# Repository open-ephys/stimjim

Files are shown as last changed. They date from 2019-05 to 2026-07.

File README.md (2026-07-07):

Stimjim - a flexible, precise, and inexpensive open-source stimulator
-------------------------------
Stimjim is a current and voltage stimulator for stimulating neural tissue (as with stimulating electrodes). 

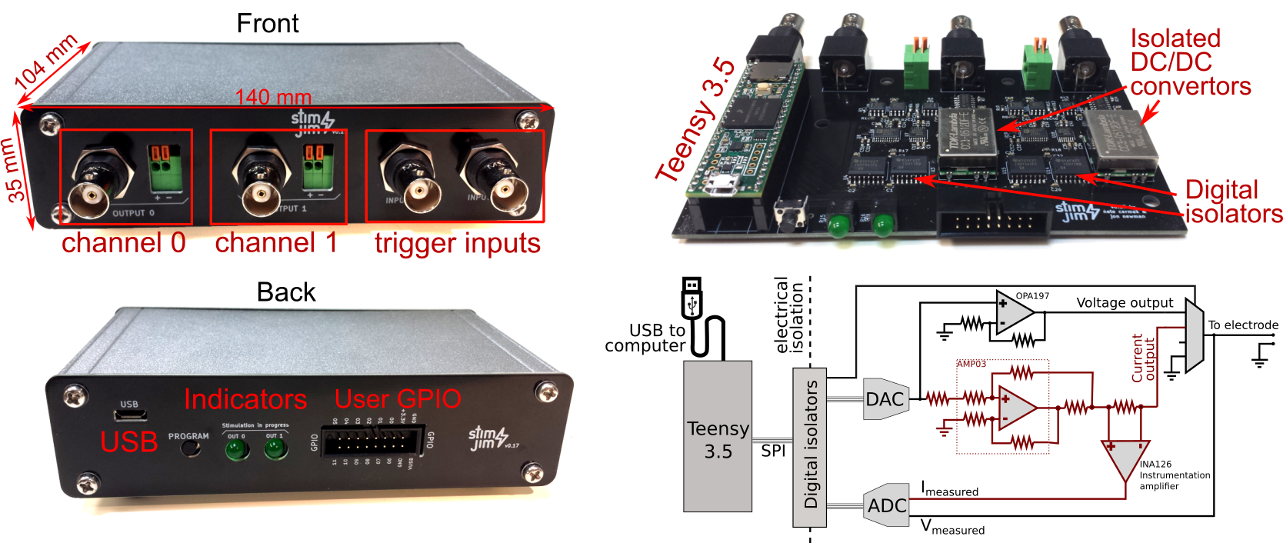
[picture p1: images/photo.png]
Stimjim picture


# Specifications:

 - Two independently-controllable output channels, each with both current and voltage output modes
 - Output range in current mode: -3.33mA to +3.33mA. 
 - Output range in voltage mode: -15V to 15V.
 - Pulse width down to 0.02 ms (as configured with default firmware)
 - Compliance voltage is +-13.7V in current mode (+/-3.33uA output possible for resistances up to 4k, +-137uA possible for resistances up to 100k)
 - Powered by USB
 - Channels are isolated from power supply and from each other.
 - Onboard ADC measurement of actual output current or voltage
 
# Building your own Stimjim:

Here are the steps to build your very own Stimjim box. 

### Option 1: Assemble (solder components onto) the board yourself.

1. Order printed circuit boards (PCBs) for the [main board](./PCB/stimjimFabricationFiles_v0.181.zip) (4-layer, 129x79.5 mm, otherwise standard order parameters) and the [enclosure front and back panels](./PCB/stimjimPanelFabricationFiles_v0.18.zip) (1-layer, 2 designs, total size 140x71 mm) from [JLCPCB](https://jlcpcb.com/), [Seeedstudio](https://www.seeedstudio.com/fusion_pcb.html) or any other PCB manufacturer. Note that for the panels, the PCB manufacturer may alert you to the fact that there is no exposed copper. This is correct, there should be a copper layer entirely covered by soldermask.
2. Order [components](./stimjim_BOM.xlsx) (entirely from [Digikey](https://www.digikey.com/)).
3. Solder components onto the PCB, using the [schematic](./schematic.pdf) and [layout](./pcb.pdf) files for reference. This may take a few hours, depending on your soldering experience and capability. I typically use a pair of good tweezers, leaded solder paste, and a soldering iron, although a reflow oven also will work as well and may be easier.

### Option 2: Use [SeeedStudio's assembly service](https://www.seeedstudio.com/fusion_pcb.html). 
Recent estimate is about $800 for two assembled boards, plus another roughly $100 for the enclosure and panels. Thanks to Vincent Prevosto for trying this out and submitting these instructions!

1.  The main board PCB and components can be ordered and assembled together on SeeedStudio.
    To order assembled boards, go to [https://www.seeedstudio.com/fusion_pcb.html](https://www.seeedstudio.com/fusion_pcb.html).
   
    *   Click on **Add Gerber Files** and upload [the main board Gerber files](./PCB/stimjimFabricationFiles_v0.181.zip). 
        Make sure to select 4 layers and enter correct dimensions (129x79.5 mm). 
        Select PCB quantity (minimum 5).
    *   Move now to the **PCB Assembly** section.
    *   Click on **Add Assembly Drawing & Pick and Place File** and upload the [zip file containing pdf assembly files and position files](./PCB/stimjim_SeeedStudioAssembly_PickAndPlace.zip).
    *   Select the requested PCB assembly quantity (tested with 2 for $780 USD in late 2019).
    *   Click on **Add BOM File** and upload the [Seeedstudio-formatted Bill of Materials](./PCB/stimjim_SeeedStudioAssembly_BOM.xlsx). The service will check parts availability. Seeedstudio may not be able to provide an instant quote, but they should send you one within a day.
    *   Seeedstudio-assembled Stimjims have been successfully tested by one user, but you have the option to have SeeedStudio test the assembly as well.
   
2. Order the [front and back panels for the enclosure](./PCB/stimjimPanelFabricationFiles_v0.18.zip) (1-layer, 2 designs, total size 140x71 mm) from [Seeedstudio](https://www.seeedstudio.com/fusion_pcb.html), [JLCPCB](https://jlcpcb.com/) or any other PCB company you like.
3. Order the enclosure itself (see the line "enclosure" in the [Bill of materials](./stimjim_BOM.xlsx)) from [Digikey](https://www.digikey.com/).

### Continuing from either option 1 or 2:

4.  Put the main board inside the enclosure (bottom slot), and screw the panels onto the front and back of the enclosure. 
5.  Connect the Stimjim to the computer via USB. Compile and download the [firmware](./stimjimPulser/) onto the Teensy, using the [Arduino IDE](https://www.arduino.cc/en/main/software) with [Teensyduino](https://www.pjrc.com/teensy/td_download.html) installed (or write your own!). Before compiling stimjimPulser.ino, You will need to install the Stimjim library by copying the [stimjim library folder](./lib/) to the appropriate arduino "libraries" folder on your computer. On Windows, this is typically My Documents/Arduino/libraries and on linux it is typically ~/Arduino/libraries. 
6.  Upon bootup, Stimjim should self-report (via the serial connection, visible using the "Serial Monitor" tool in the Arduino IDE) on a handful of calibration routines it runs. Example output looks as follows:

	    Booting StimJim on Teensy 3.5!
	    Initializing inputs...
	    ADC offsets (+-2.5V): -11.030000, -11.150000
	    ADC offsets (+-10V): -10.220000, -10.340000
	    current offsets: 11, 8
	    voltage offsets: 0, 0
	    Ready to go!
	   
	The ADC offsets indicate the ADC reading (in ADC units, 2.4mV per ADC unit) from the output when the output is grounded, for channels 0 and 1, respectively. The ADC typically has a small but nonzero "Zero offset error" which is the reading when it should be reading exactly 0V. Stimjim measures this error (with two different range settings) and corrects all subsequent readings. We typically see values less than 20 - a value of +-4096 indicates some sort of problem with the board.
	
	Current offsets are the raw value of the DAC output (-32768 to 32767) that yields the current reading closest to 0uA. This offset is also used in subsequent stimulation to avoid any small but consistent DC current during pulses.

# Getting started using Stimjim:

To generate a pulse train, you first need to send a serial command, terminated by a newline (\n) in order to define a PulseTrain. An example command would be:

    S0,0,1,2000,1000000; 100,0,150; -100,-100,200
   
The "S" is to *s*pecify the parameters of a pulse train, and the zero immediately following the S implies that we are going to set parameters for PulseTrain 0. The code provided here allows Stimjim to store 100 different PulseTrain parameter sets. If any comma- and semicolon-separated numbers appear following the S, they are the pulse train parameters. A command that simply consists of "S0" will result in simply printing out the current parameters of PulseTrain 0. 

Once a PulseTrain is defined, to run it you would send a command of the form:

    T0

This tells Stimjim to start running PulseTrain 0. If we had parameterized PulseTrain #3, we could just as easily run PulseTrain #3 with the command "T3".

##  Parameterization 



The numbers that come after an "S" indicate parameters as denoted below:

1. [PulseTrain number], 
2. [output 0 mode],
3. [output 1 mode],
4. [period],
5. [duration];
6. [mV or uA for stage 0 output 0],
7. [mV or uA for stage 0 output 1],
8. [stage 0 duration (us)]; 
9. [mV or uA for stage 1 output 0],
10. [mV or uA for stage 1 output 1],
11. [stage 1 duration (us)];
12. (etc for additional stages, up to 10 total stages).

After the "S", the first parameter is the number of the PulseTrain that we are defining. The next two parameters are the modes of each output channels. Modes are as follows:

 - 0 = Voltage output
 - 1 = Current output
 - 2 = Output is disconnected
 - 3 = Output is grounded

Our example command above was: 
   
    S0,0,1,2000,1000000; 100,0,150; -100,-100,200
   
In this example, output 0 is generating a voltage output (mode 0), and output 1 is generating a current output (mode 1). To specify that a channel should not output anything during a pulse train, set the mode to 3 (ground).  

The fourth parameter is the _period_ of the pulse train. In this example, pulses are delivered every 2000 us (2 ms).

The fifth parameter is the _duration_ of the pulse train, in microseconds. In the example, the pulse train lasts for one second (1000000 microseconds).

Parameters after the 5th come in sets of 3, and describe a "stage" of a pulse in the train.  The first two parameters are the amplitude (in mV or uA, depending on whether the output is voltage or current) of each channel during that stage, and the third is the duration (in microseconds) of that stage. Note that a semi-colon is before the beginning of each set of 3, and the three parameters themselves are separated from each other by commas.

In the example given above, there are two stages to each pulse. In the first, channel 0 outputs 100mV, channel 1 outputs nothing, and that lasts for 150 usec. Then channel 0 switches to outputting -100mV, and channel 2 outputs -100uA for 200 usec. 

## Triggering
Stimjim can utilize trigger signals from its BNC inputs. To make a rising edge on input 0 trigger PulseTrain 1, send the command

	R0,1

To make a rising edge on input 1 trigger PulseTrain 2

	R1,2
	
And finally, to make a falling edge on input 1 trigger PulseTrain 2:

	R1,2,1

The final argument for the R command is optional, and defaults to 0 (rising edge).

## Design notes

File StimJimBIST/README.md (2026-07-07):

# StimJimBIST
A simple console application that performs built in evaluation of the funcationility
of both stimulation channels.

Limitations:
- Assumes that StimJimPulser is loaded onto the Teensy
- Does not test physical connectivity (solder joints) of BNCS, screw-terminals
- Does not test trigger or GPIO capabilities
- Assumes there is nothing connected to the output channels of the device

### Usage
Usage:
```
StimJimBIST COM3
```

Example result:
```
Running StimJim BIST.
Testing voltage mode.

Channel 0:
| Test V. | Meas V. | Err. mV. | Pass / Fail | Test uA. | Meas uA. | Err. uA | Pass / Fail |
|---------|---------|----------|-------------|----------|----------|---------|-------------|
| -9.00   | -8.99   | 7        | PASS        | -1993.36 | -1987.00 | 6.36    | PASS        |
| 0.00    | 0.01    | 7        | PASS        | 0.00     | 0.00     | 0.00    | PASS        |
| 9.00    | 9.01    | 5        | PASS        | 1993.36  | 1982.00  | -11.36  | PASS        |

Channel 1:
| Test V. | Meas V. | Err. mV. | Pass / Fail | Test uA. | Meas uA. | Err. uA | Pass / Fail |
|---------|---------|----------|-------------|----------|----------|---------|-------------|
| -9.00   | -9.00   | 3        | PASS        | -1993.36 | -1985.00 | 8.36    | PASS        |
| 0.00    | 0.01    | 5        | PASS        | 0.00     | 0.00     | 0.00    | PASS        |
| 9.00    | 9.02    | 19       | PASS        | 1993.36  | 1984.00  | -9.36   | PASS        |

Testing current mode.

Channel 0:
| Pol. | Meas V. | Err. mV. | Pass / Fail | Meas uA. | Err. uA | Pass / Fail |
|------|---------|----------|-------------|----------|---------|-------------|
| -    | -9.98   | 21       | PASS        | -4.00    | -4.00   | PASS        |
| +    | 10.01   | 6        | PASS        | 0.00     | 0.00    | PASS        |

Channel 1:
| Pol. | Meas V. | Err. mV. | Pass / Fail | Meas uA. | Err. uA | Pass / Fail |
|------|---------|----------|-------------|----------|---------|-------------|
| -    | -9.97   | 27       | PASS        | -4.00    | -4.00   | PASS        |
| +    | 10.01   | 12       | PASS        | 0.00     | 0.00    | PASS        |

GLOBAL RESULT: PASS
```

### Explanation

#### Voltage Mode test
This test examines the functionality of the DAC, ADC, output mux, current source, and current sense circuit simultaneously.

- Put both channels in voltage mode ()
	- This this ties V_OUT to CHANNEL_OUT, which is open
	- This ties I_OUT to ground through a 1k resistor
	- I_OUT = V_OUT / 3kOhm
	
- For each channel, apply -9V, 0V, and 9V to V_OUT
	- This sets V_DAC = V_OUT / 1.5
	- V_DAC is still applied to Howland and current measurement circuit with transimpedance gain of 0.33 mA per volt
	- Read the voltage at CHANNEL_OUT to see if the voltage iset to the test voltage
	- Read I_SENSE to see that its equal to V_DAC / 1.5 * 0.33 mA/V

#### Current Mode test
This test examines the functionality of the DAC, ADC, and output mux, and current sense circuit simultaneously.
It is largely redundant with the first test but does ensure that the output mux can switch to a non default state.

- Put both channels in current mode
	- This ties V_OUT to floating
    - This ties I_OUT to CHANNEL_OUT, which is open

- For each channel, attempt to apply  -1V, 1V to V_OUT
	- This sets V_DAC = V_OUT / 1.5
	- This attempts to deliver V_DAC * 0.33 mA/V to CHANNEL_OUT
	- Read the voltage at CHANNEL_OUT (should saturate at +/-10V)
	- Read current through CHANNEL_OUT (should be 0 since its open)

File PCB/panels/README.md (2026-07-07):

EXN-23359.DXF is the original outline of the extruded aluminum enclosure. It was
edited in panel-outline.SLDPRT to remove some of the finer features of the
aluminum enclosure that might not be good PCB DFM. I extruded the sketch in
panel-outline.SLDPRT because exporting the sketch by itself was presenting buggy
behavior wherein not all lines of the sketch were actually exported into the
resulting DXF. Instead, I export the outline of the extruded part which doesn't
present this buggy behavior. panel-outline.SLDPRT is exported to
panel-outline.DXF which is subsequently imported into the KiCAD PCB panel files
as a graphic.

The channel-design.SLDPRT is used to create the silkscreen design for each channel.

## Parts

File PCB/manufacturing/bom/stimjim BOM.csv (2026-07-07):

# | Qty | Reference | Value | Tolerance | Footprint | TempCo | Voltage | DNP | OEPSPN | MPN | Description
1 | 40 | C1,C2,C6,C7,C9,C11,C13,C14,C16,C17,C18,C20,C22,C23,C24,C25,C26,C27,C31,C32,C34,C35,C38,C39,C41,C42,C43,C44,C47,C48,C49,C50,C63,C65,C66,C67,C80,C82,C89,C90 | 0.1uF |  | Capacitor_SMD:C_0603_1608Metric |  |  |  | OEPS010009 | GRM188R72A104KA35D | CAPACITOR: SMD CER 0603 100nF 100V ±10% X7R [GRM188R72A104KA35D] [SMD]
2 | 6 | C3,C4,C5,C28,C29,C30 | 10uF |  | Capacitor_SMD:C_1206_3216Metric_Pad1.33x1.80mm_HandSolder |  | 25V |  | OEPS010094 | GRT319R6YA106KE01D | CAPACITOR: SMD CER 1206 10uF 35V ±10% X5R [GRT319R6YA106KE01D] [SMD]
3 | 12 | C8,C10,C12,C15,C33,C36,C37,C40,C51,C52,C295,C297 | 1uF |  | Capacitor_SMD:C_0603_1608Metric | X5R | 25V |  | OEPS010022 | CL10A105KA8NNNC | CAPACITOR: SMD CER 0603 1uF 25V ±10% X5R [CL10A105KA8NNNC] [SMD]
4 | 4 | C19,C21,C45,C46 | 0.01uF |  | Capacitor_SMD:C_0603_1608Metric |  |  |  | OEPS010074 | C1608X7R1H103K080AA | CAPACITOR: SMD CER 0603 10nF 50V ±10% X7R [C1608X7R1H103K080AA] [SMD]
5 | 2 | C53,C54 | 2.2nF |  | Capacitor_SMD:C_1210_3225Metric_Pad1.33x2.70mm_HandSolder |  |  | DNP | OEPS000000 | DNP | DNP: Do Not Populate (DNI)
6 | 12 | C55,C56,C57,C58,C59,C60,C61,C62,C64,C81,C83,C84 | 0.1uF |  | Capacitor_SMD:C_0402_1005Metric | X7R |  |  | OEPS010050 | C1005X7R1E104K050BB | CAPACITOR: SMD CER 0402 100nF 25V ±10% X7R (OEPS H02 001) [C1005X7R1E104K050BB] [SMD]
7 | 8 | C68,C69,C72,C73,C74,C75,C76,C77 | 10uF |  | Capacitor_SMD:C_0603_1608Metric |  |  |  | OEPS010093 | GRM188R6YA106MA73J | CAPACITOR: SMD CER 0603 10uF 35V ±20% X5R [GRM188R6YA106MA73J] [SMD]
8 | 2 | C70,C71 | 22p |  | Capacitor_SMD:C_0402_1005Metric |  |  |  | OEPS010080 | CL05C220JB51PNC | CAPACITOR: SMD CER 0402 22pF 50V ±5% C0G/NP0 [CL05C220JB51PNC] [SMD]
9 | 2 | C78,C79 | 10p |  | Capacitor_SMD:C_0603_1608Metric |  |  |  | OEPS010096 | C0603C100J5GACTU | CAPACITOR: SMD CER 0603 10pF 50V ±5% C0G [C0603C100J5GACTU] [SMD]
10 | 4 | C85,C86,C87,C88 | 4.7u |  | Capacitor_SMD:C_0402_1005Metric | X5R | 16V |  | OEPS010097 | KGM05CR51C475MH | CAPACITOR: SMD CER 0402 4.7uF 16V ±20% X5R [KGM05CR51C475MH] [SMD]
11 | 4 | C91,C92,C93,C94 | 4.7u |  | Capacitor_SMD:C_0603_1608Metric |  |  |  | OEPS010047 | GRM188R61E475KE11D | CAPACITOR: SMD CER 0603 4.7uF 25V ±10% X5R (OEPS J05 009) [GRM188R61E475KE11D] [SMD]
12 | 10 | D1,D6,D8,D10,D11,D12,D13,D14,D15,D16 | BAT54SW |  | Package_TO_SOT_SMD:SOT-323_SC-70 |  |  |  | OEPS030056 | BAT54SW | DIODE: DIODE SCHOTTKY 30V 340mA ARRAY [BAT54SW] [TH]
13 | 3 | D3,D4,D5 | LED |  | open-ephys:LUMEX_SSF-LHXH100GD-01 |  |  |  | OEPS030055 | SSF-LXH100GD-01 | DIODE: LED TH Green 565nm 20mA R/A [SSF-LXH100GD-01] [TH]
14 | 1 | D9 | TPD4E05U06DQA |  | Package_SON:USON-10_2.5x1.0mm_P0.5mm |  |  |  | OEPS030037 | TPD4E05U06DQAR | DIODE: TVS DIODE 5.5VWM 14VC [TPD4E05U06DQAR] [10-UFDFN]
15 | 1 | J1 | 302-R161 |  | Connector_IDC:IDC-Header_2x08_P2.54mm_Horizontal |  |  |  | OEPS070152 | 302-R161 | CONNECTOR: HEADER 2.54MM R/A 2x8POS [302-R161] [TH]
16 | 4 | J2,J3,J7,J9 | 0731375003 |  | Connector_Coaxial:BNC_Amphenol_B6252HB-NPP3G-50_Horizontal |  |  |  | OEPS070151 | 0731375003 | CONNECTOR: BNC JACK 50ohm R/A [0731375003] [TH]
17 | 1 | J4 | 10129383-910002ALF |  | Connector_PinHeader_2.54mm:PinHeader_2x04_P2.54mm_Vertical_SMD |  |  | DNP | OEPS070120 | 10129383-910002ALF | CONNECTOR: HEADER VERT 2x5POS 2.54MM [10129383-910002ALF] [SMD]
18 | 1 | J10 | USB4105-GF-A |  | Connector_USB:USB_C_Receptacle_GCT_USB4105-xx-A_16P_TopMnt_Horizontal |  |  |  | OEPS070105 | USB4105-GF-A | CONNECTOR: USB2.0 TYPE C 24P SMD R/A [USB4105-GF-A] [SMD/TH]
19 | 1 | J11 | BM03B-SRSS-TB |  | Connector_JST:JST_SH_BM03B-SRSS-TB_1x03-1MP_P1.00mm_Vertical |  |  | DNP | OEPS070121 | BM03B-SRSS-TB | CONNECTOR: HEADER VERT 3POS 1MM [BM03B-SRSS-TB] [SMD]
20 | 1 | L1 | AOTA-B201610S3R3-101-T |  | open-ephys:L_Abracon_2x1.6x1.0mm |  |  |  | OEPS040036 | AOTA-B201610S3R3-101-T | INDUCTOR: FIXED INDUCTOR SMD 3.3uH 2.1A 140mΩ [AOTA-B201610S3R3-101-T] [0806]
21 | 1 | N1 | SMTRAM3-7-5ET |  | open-ephys:SMTRA_M3-7-5ET |  |  |  | OEPS100089 | SMTRAM3-7-5ET | OTHER: SURFACE MOUNT R'ANGLE M3 [SMTRAM3-7-5ET] [Other]
22 | 2 | R1,R8 | 10k | 0.1% | Resistor_SMD:R_0603_1608Metric |  |  |  | OEPS020235 | RG1608P-103-B-T5 | RESISTOR: SMD 0603 10kΩ ±0.1% 0.100W [RG1608P-103-B-T5] [SMD]
23 | 2 | R2,R4 | 3k | 1% | Resistor_SMD:R_0603_1608Metric |  |  |  | OEPS020234 | RG1608P-302-B-T5 | RESISTOR: SMD 0603 3kΩ ±0.1% 0.100W [RG1608P-302-B-T5] [SMD]
24 | 2 | R3,R10 | 5k | 0.1% | Resistor_SMD:R_0603_1608Metric |  |  |  | OEPS020233 | RG1608P-4991-B-T5 | RESISTOR: SMD 0603 4.99kΩ ±0.1% 0.100W [RG1608P-4991-B-T5] [SMD]
25 | 2 | R5,R12 | 100 | 0.1% | Resistor_SMD:R_0603_1608Metric |  |  |  | OEPS020232 | RG1608P-101-B-T5 | RESISTOR: SMD 0603 100Ω ±0.1% 0.100W [RG1608P-101-B-T5] [SMD]
26 | 2 | R6,R13 | 360 | 0.1% | Resistor_SMD:R_0603_1608Metric |  |  |  | OEPS020231 | RG1608P-361-B-T5 | RESISTOR: SMD 0603 360Ω ±0.1% 0.100W [RG1608P-361-B-T5] [SMD]
27 | 3 | R7,R14,R27 | 1k | 1% | Resistor_SMD:R_0603_1608Metric |  |  |  | OEPS020215 | RG1608P-102-B-T5 | RESISTOR: SMD 0603 1kΩ ±0.1% 0.100W [RG1608P-102-B-T5] [SMD]
28 | 2 | R9,R11 | 0 |  | Resistor_SMD:R_0603_1608Metric |  |  |  | OEPS020151 | RCS06030000Z0EA | RESISTOR: SMD 0603 0Ω 1A [RCS06030000Z0EA] [SMD]
29 | 4 | R15,R17,R18,R32 | 10k |  | Resistor_SMD:R_0603_1608Metric |  |  |  | OEPS020133 | RC0603FR-0710KL | RESISTOR: SMD 0603 10kΩ ±1% 0.100W [RC0603FR-0710KL] [SMD]
30 | 10 | R16,R21,R22,R23,R24,R25,R36,R37,R38,R39 | 270 |  | Resistor_SMD:R_0805_2012Metric |  |  |  | OEPS020024 | CRCW0805270RFKEAHP | RESISTOR: SMD 0805 270Ω ±1% 0.500W [CRCW0805270RFKEAHP] [SMD]
31 | 2 | R19,R20 | 2.2M |  | Resistor_SMD:R_1210_3225Metric_Pad1.30x2.65mm_HandSolder |  |  |  | OEPS020230 | CRGCQ1210J2M2 | RESISTOR: SMD 1210 2.2MΩ ±5% 0.5W [CRGCQ1210J2M2] [SMD]
32 | 3 | R26,R34,R35 | 200 |  | Resistor_SMD:R_0603_1608Metric |  |  |  | OEPS020141 | RC0603FR-07200RL | RESISTOR: SMD 0603 200Ω ±1% 0.100W (OEPS J30 017) [RC0603FR-07200RL] [SMD]
33 | 2 | R28,R29 | 100 | 1% | Resistor_SMD:R_0603_1608Metric |  |  |  | OEPS020042 | CRCW0603100RFKEAHP | RESISTOR: SMD 0603 100Ω ±1% 0.333W [CRCW0603100RFKEAHP] [SMD]
34 | 3 | R30,R31,R33 | 27 |  | Resistor_SMD:R_0402_1005Metric |  |  |  | OEPS020170 | RMCF0402FT27R0 | RESISTOR: SMD 0402 27Ω ±1% 0.063W [RMCF0402FT27R0] [SMD]
35 | 2 | R266,R267 | 5.1k | 1% | Resistor_SMD:R_0402_1005Metric |  |  |  | OEPS020173 | ERJ-2RKF5101X | RESISTOR: SMD 0402 5.1kΩ ±1% 0.100W [ERJ-2RKF5101X] [SMD]
36 | 1 | SW2 | PTS645VH58-2 LFS |  | Button_Switch_THT:SW_Tactile_SPST_Angled_PTS645Vx58-2LFS |  |  |  | OEPS070114 | PTS645VH58-2 LFS | CONNECTOR: SWITCH TACTILE SPST-NO 0.05A 12V [PTS645VH58-2 LFS] [TH]
37 | 1 | SW3 | TS04-66-50-BK-160-SMT |  | open-ephys:SAMESKY_TS04-66-XX-BK-XXX-SMT-XX |  |  |  | OEPS070115 | TS04-66-50-BK-160-SMT | CONNECTOR: SWITCH TACTILE SPST-NO TOP ACTUATED [TS04-66-50-BK-160-SMT] [SMD]
38 | 6 | U1,U9,U10,U20,U21,U26 | OPA197 |  | Package_SO:SOIC-8_3.9x4.9mm_P1.27mm |  |  |  | OEPS080229 | OPA197IDR | IC: OPAMP GP 1 CIRCUIT [OPA197IDR] [8-SOIC]
39 | 2 | U2,U13 | CC3-0512DF-E |  | microstim:CC3-0512DF-E |  |  |  | OEPS100043 | CC3-0512DF-E | OTHER: DC DC CONVERTER +/-12V TO +/-15V 3W [CC3-0512DF-E] [Populated PCB]
40 | 2 | U3,U14 | ISO7760 |  | Package_SO:SOIC-16W_7.5x10.3mm_P1.27mm |  |  |  | OEPS080228 | ISO7760DWR | IC: DIGITAL ISOLATOR 6 Channel [ISO7760DWR] [16-SOIC]
41 | 2 | U4,U15 | ISO7741 |  | Package_SO:SOIC-16W_7.5x10.3mm_P1.27mm |  |  |  | OEPS080227 | ISO7741DWR | IC: DIGITAL ISOLATOR 4 Channel [ISO7741DWR] [16-SOIC]
42 | 2 | U5,U16 | MC78L05ACDR2G |  | Package_SO:SOIC-8_3.9x4.9mm_P1.27mm |  |  |  | OEPS080226 | MC78L05ACDR2G | IC: LDO 5V 100mA [MC78L05ACDR2G] [8-SOIC]
43 | 2 | U6,U17 | AD5752 |  | Package_SO:TSSOP-24_4.4x7.8mm_P0.65mm |  |  |  | OEPS080091 | AD5752AREZ | IC: DAC 16BIT [AD5752AREZ] [24-TSSOP]
44 | 2 | U7,U18 | AD7321 |  | Package_SO:TSSOP-14_4.4x5mm_P0.65mm |  |  |  | OEPS080225 | AD7321BRUZ-REEL7 | IC: ADC 14BIT SAR 2 channels [AD7321BRUZ-REEL7] [14-TSSOP]
45 | 2 | U8,U19 | AD1582 |  | Package_TO_SOT_SMD:SOT-23 |  |  |  | OEPS080224 | AD1582ARTZ-REEL7 | IC: VREF 2.5V 0.8% 5mA [AD1582ARTZ-REEL7] [SOT-23-3]
46 | 2 | U12,U23 | DG409DYZ-T |  | Package_SO:SO-16_3.9x9.9mm_P1.27mm |  |  |  | OEPS080223 | DG409DYZ-T | IC: MULTIPLEXER 2 X 4:1 [DG409DYZ-T] [16-SOIC]
47 | 2 | U24,U29 | AD8421 |  | Package_SO:SOIC-8_3.9x4.9mm_P1.27mm |  |  |  | OEPS080222 | AD8421BRZ-R7 | IC: INST AMP 1 CIRCUIT [AD8421BRZ-R7] [8-SOIC]
48 | 1 | U25 | W25Q128JVS |  | Package_SO:SOIC-8_5.3x5.3mm_P1.27mm |  |  |  | OEPS080163 | W25Q128JVSIQ | IC: FLASH 128MBIT SPI/QUAD [W25Q128JVSIQ] [8-SOIC]
49 | 2 | U27,U28 | LT1995 |  | Package_SO:MSOP-10_3x3mm_P0.5mm |  |  |  | OEPS080221 | LT1995CMS#PBF | IC: OPAMP PGA 1 CIRCUIT [LT1995CMS#PBF] [10-MSOP]
50 | 1 | U30 | RP2354B |  | Package_DFN_QFN:QFN-80-1EP_10x10mm_P0.4mm_EP3.4x3.4mm |  |  |  | OEPS080220 | SC1512-A4 | IC: MCU ARM RP2354B0A4 [SC1512-A4] [QFN-80]
51 | 1 | U151 | AP2112K-3.3 |  | Package_TO_SOT_SMD:SOT-23-5 |  |  |  | OEPS080155 | AP2112K-3.3TRG1 | IC: LDO 3.3V 600mA [AP2112K-3.3TRG1] [SOT-23-5]
52 | 1 | Y1 | ABM8AIG-12.000MHZ-12-2Z-T3 |  | Crystal:Crystal_SMD_Abracon_ABM8AIG-4Pin_3.2x2.5mm |  |  |  | OEPS100059 | ABM8AIG-12.000MHZ-12-2Z-T3 | OTHER: Crystal 12 MHz ±20ppm 12pF 100Ohms [ABM8AIG-12.000MHZ-12-2Z-T3] [SMD]

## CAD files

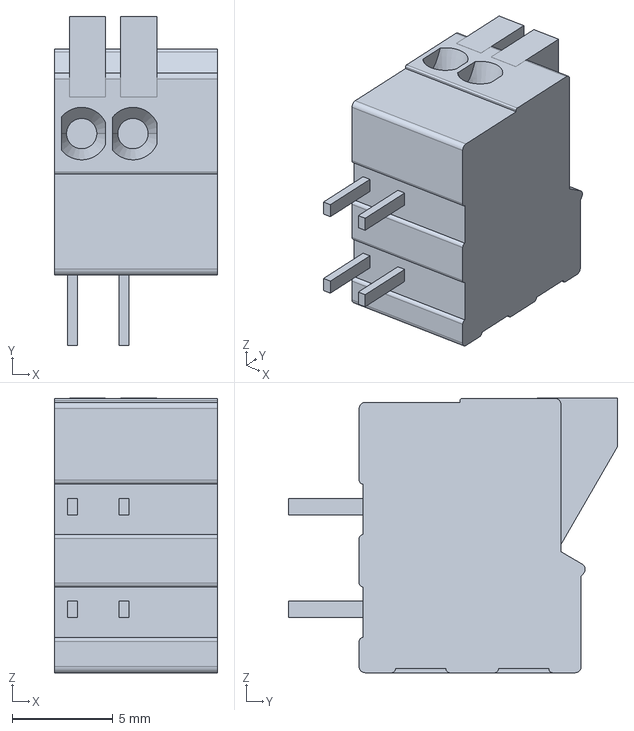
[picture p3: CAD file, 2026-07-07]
PCB/footprints/c-1-2834016-2-1-3d.stp
8.08 x 16.3 x 13.6 mm

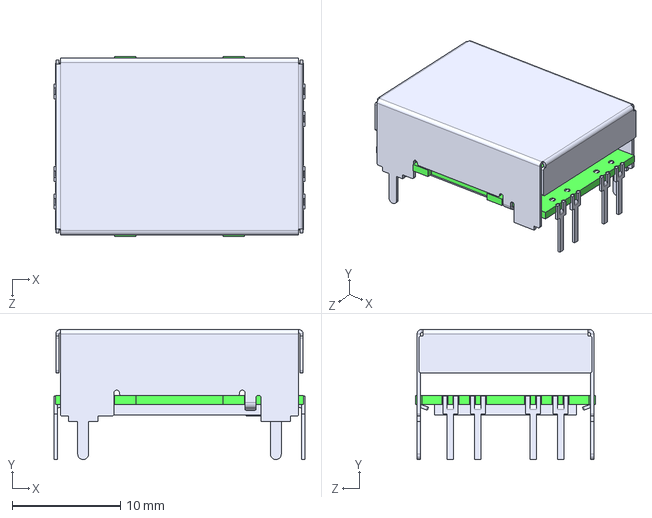
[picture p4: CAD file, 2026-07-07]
PCB/footprints/cc3-f-e_outline.STEP
23.2 x 12.0 x 16.6 mm

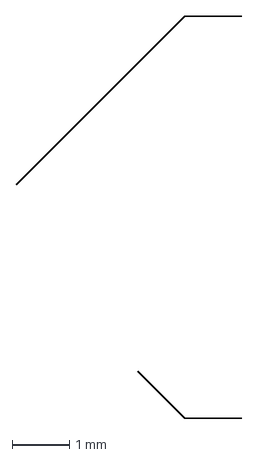
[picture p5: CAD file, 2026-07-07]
PCB/panels/channel-silkscreen_callouts.DXF
3.93 x 7.00 mm

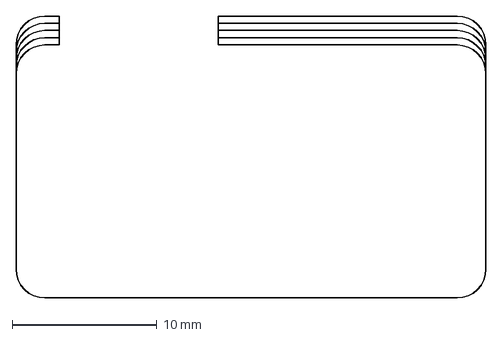
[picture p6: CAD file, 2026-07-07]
PCB/panels/channel-silkscreen_outline.DXF
32.5 x 19.5 mm

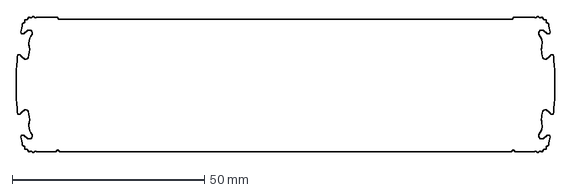
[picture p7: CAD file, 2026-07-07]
PCB/panels/EXN-23359.DXF
140.0 x 35.5 mm

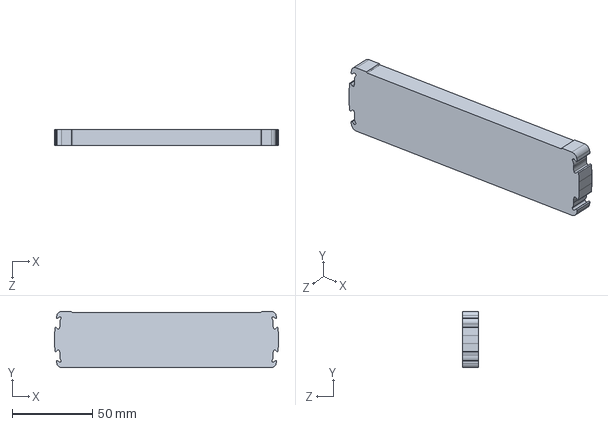
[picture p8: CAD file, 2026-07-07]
PCB/panels/panel-outline.SLDPRT
140.0 x 35.0 x 10.0 mm

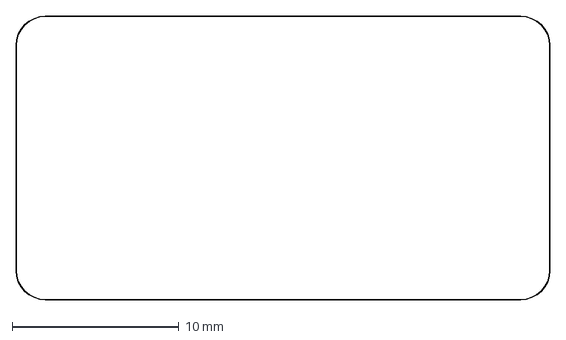
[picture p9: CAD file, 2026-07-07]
PCB/panels/channel-keepout.DXF
32.0 x 17.0 mm

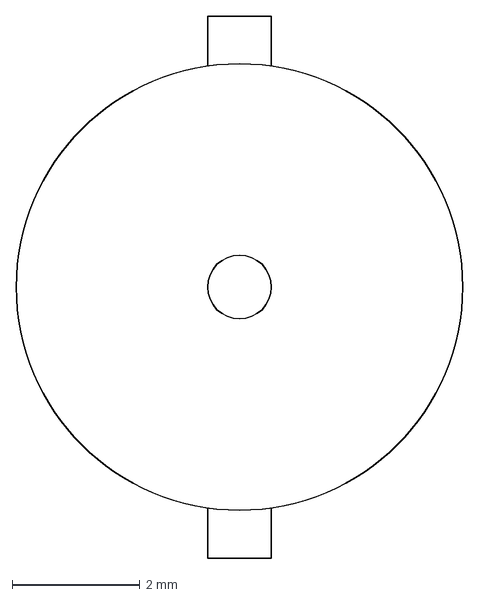
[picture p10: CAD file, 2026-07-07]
PCB/panels/channel-silkscreen_bnc.DXF
7.00 x 8.50 mm

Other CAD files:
PCB/panels/channel-design.SLDPRT
PCB/panels/panel-outline.DXF

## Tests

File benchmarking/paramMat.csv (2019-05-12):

V1 | V2 | V3 | V4 | V5 | V6 | V7 | V8 | V9 | V10
0 | 1 | 250 | 1e+06 | 5000 | 500 | 100 | -5000 | -500 | 100
0 | 1 | 325 | 1e+06 | 5000 | 500 | 100 | -5000 | -500 | 100
0 | 1 | 422 | 1e+06 | 5000 | 500 | 100 | -5000 | -500 | 100
0 | 1 | 549 | 1e+06 | 5000 | 500 | 100 | -5000 | -500 | 100
0 | 1 | 713 | 1e+06 | 5000 | 500 | 100 | -5000 | -500 | 100
0 | 1 | 927 | 1e+06 | 5000 | 500 | 100 | -5000 | -500 | 100
0 | 1 | 1205 | 1e+06 | 5000 | 500 | 100 | -5000 | -500 | 100
0 | 1 | 1566 | 1e+06 | 5000 | 500 | 100 | -5000 | -500 | 100
0 | 1 | 2035 | 1e+06 | 5000 | 500 | 100 | -5000 | -500 | 100
0 | 1 | 2645 | 1e+06 | 5000 | 500 | 100 | -5000 | -500 | 100
0 | 1 | 3437 | 1e+06 | 5000 | 500 | 100 | -5000 | -500 | 100
0 | 1 | 4467 | 1e+06 | 5000 | 500 | 100 | -5000 | -500 | 100
0 | 1 | 5806 | 1e+06 | 5000 | 500 | 100 | -5000 | -500 | 100
0 | 1 | 7546 | 1e+06 | 5000 | 500 | 100 | -5000 | -500 | 100
0 | 1 | 9807 | 1e+06 | 5000 | 500 | 100 | -5000 | -500 | 100
0 | 1 | 12746 | 1e+06 | 5000 | 500 | 100 | -5000 | -500 | 100
0 | 1 | 16565 | 1e+06 | 5000 | 500 | 100 | -5000 | -500 | 100
0 | 1 | 21529 | 1e+06 | 5000 | 500 | 100 | -5000 | -500 | 100
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

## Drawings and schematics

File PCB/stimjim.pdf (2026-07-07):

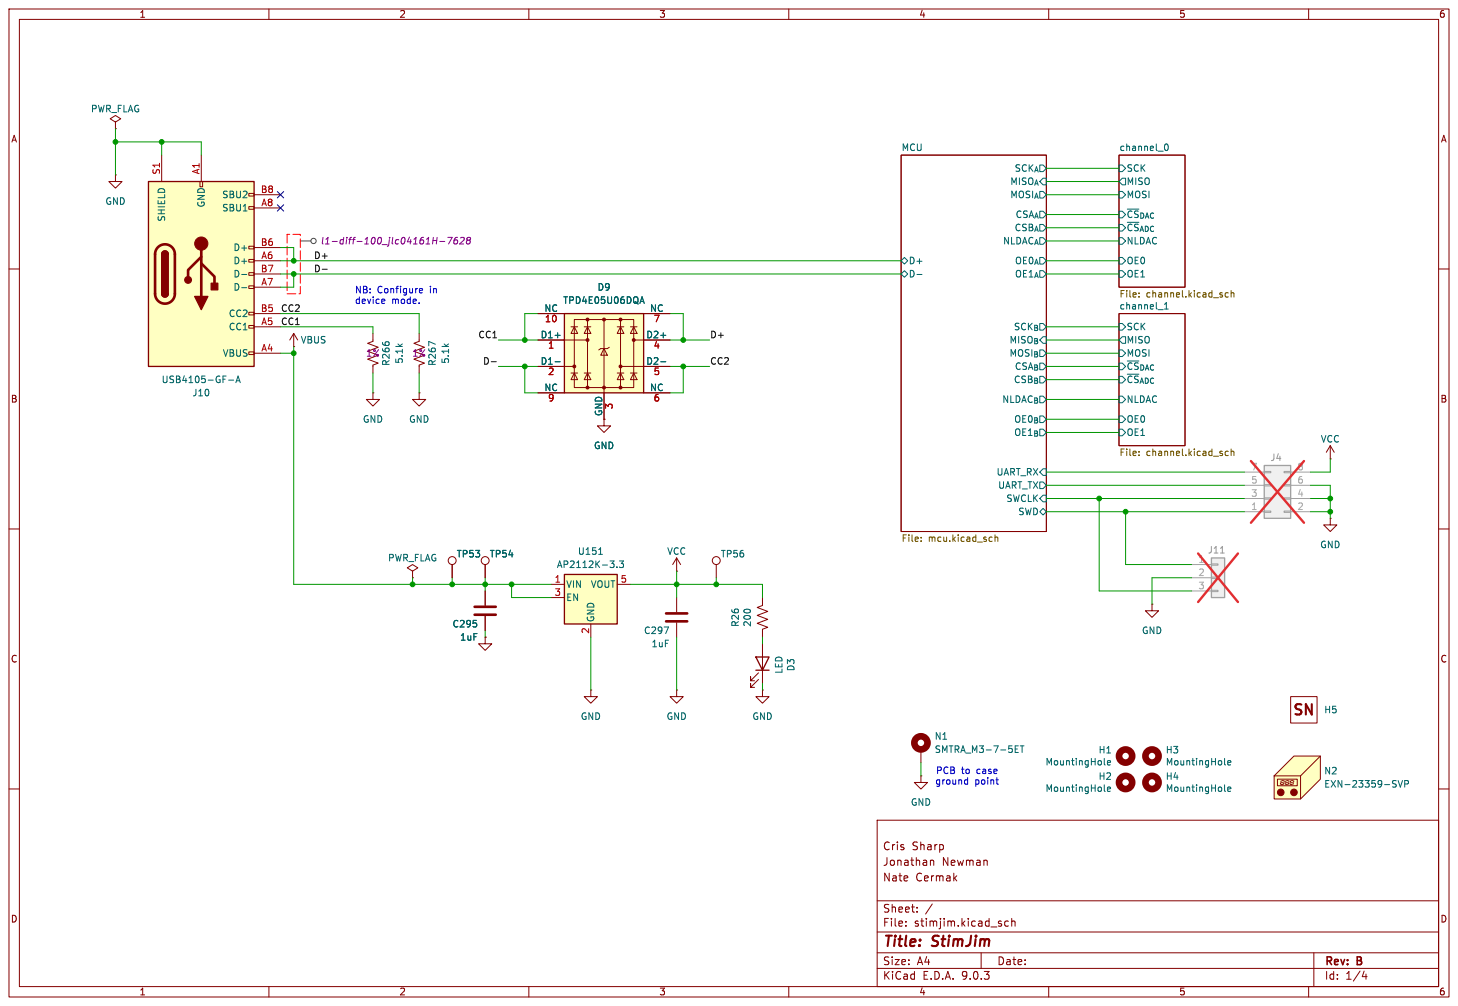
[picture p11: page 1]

~{CS}_{DAC} channel_1 File: channel.kicad_sch R266 5.1k 1%

~{CS}_{DAC} channel_0 File: channel.kicad_sch OE0 OE1 SCK MOSI MISO

2 VOUT 5 U151 AP2112K-3.3 TP53 H4 MountingHole H1 MountingHoleH2 MountingHole H3 MountingHole N1SMTRA_M3-7-5ET GND R267 5.1k 1% SHIELD S1 GND A1 VBUS A4 CC1 A5 CC2 B5 D- A7 D- B7 D+ A6 D+ B6 SBU1 A8 SBU2 B8

File: stimjim.kicad_sch Sheet: / Nate Cermak

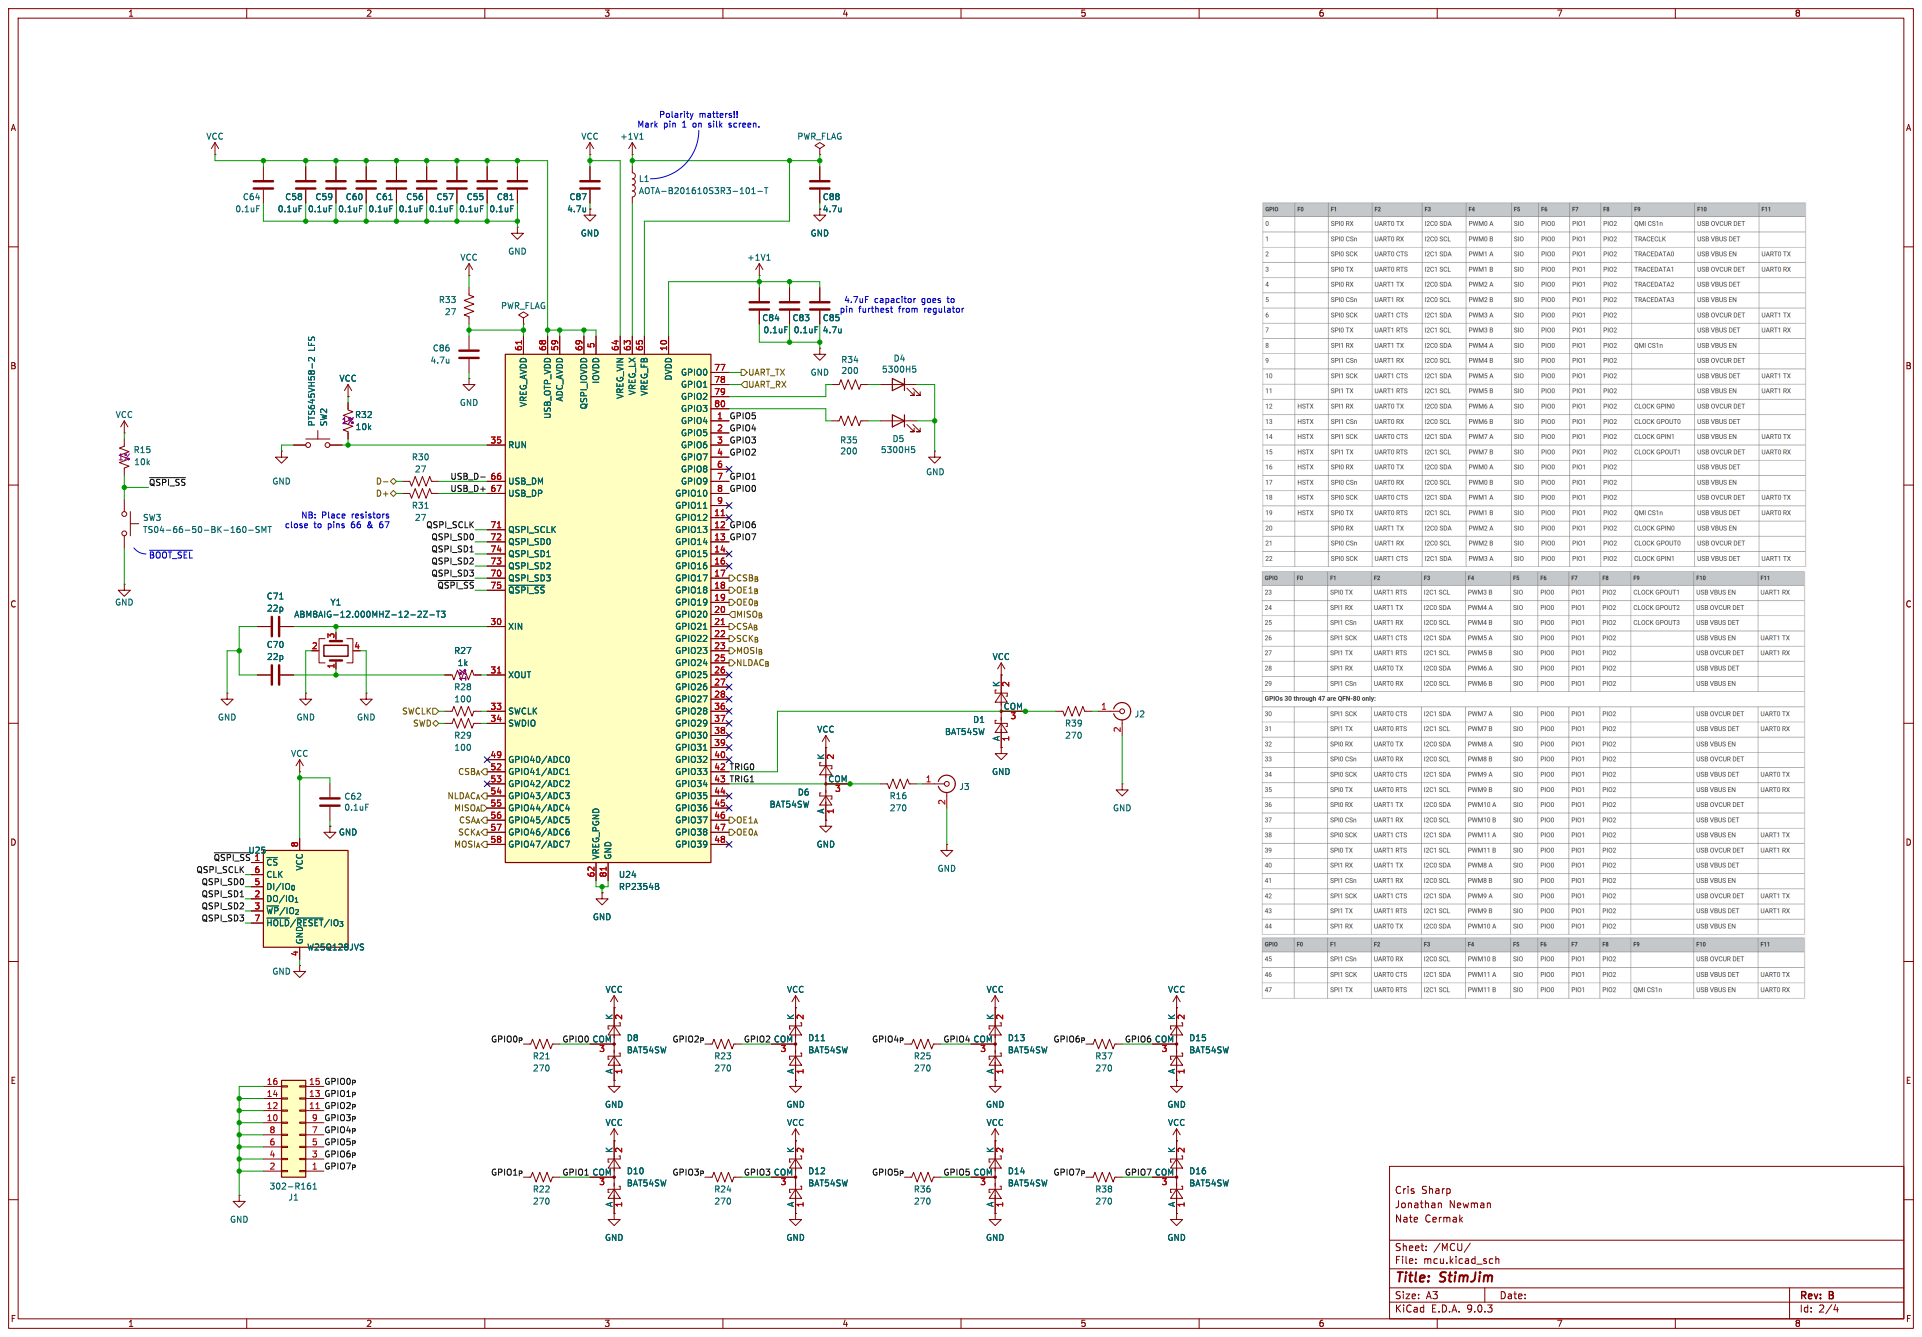
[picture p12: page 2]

File: mcu.kicad_sch Sheet: /MCU/ Nate Cermak

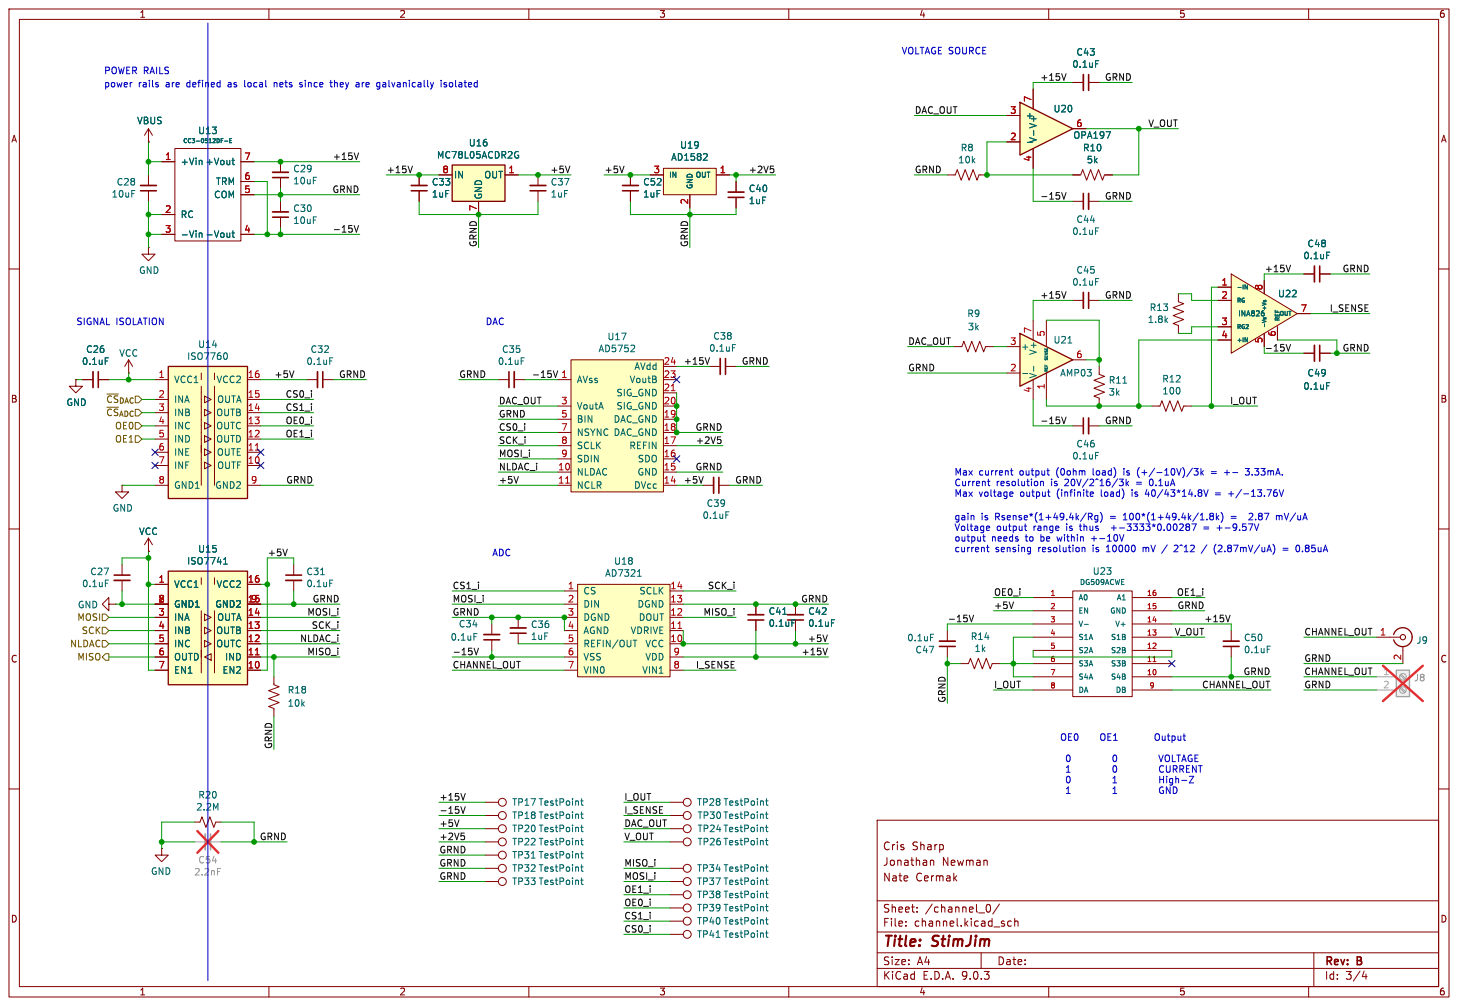
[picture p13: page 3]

output needs to be within +-10V

File: channel.kicad_sch Sheet: /channel_0/ Nate Cermak

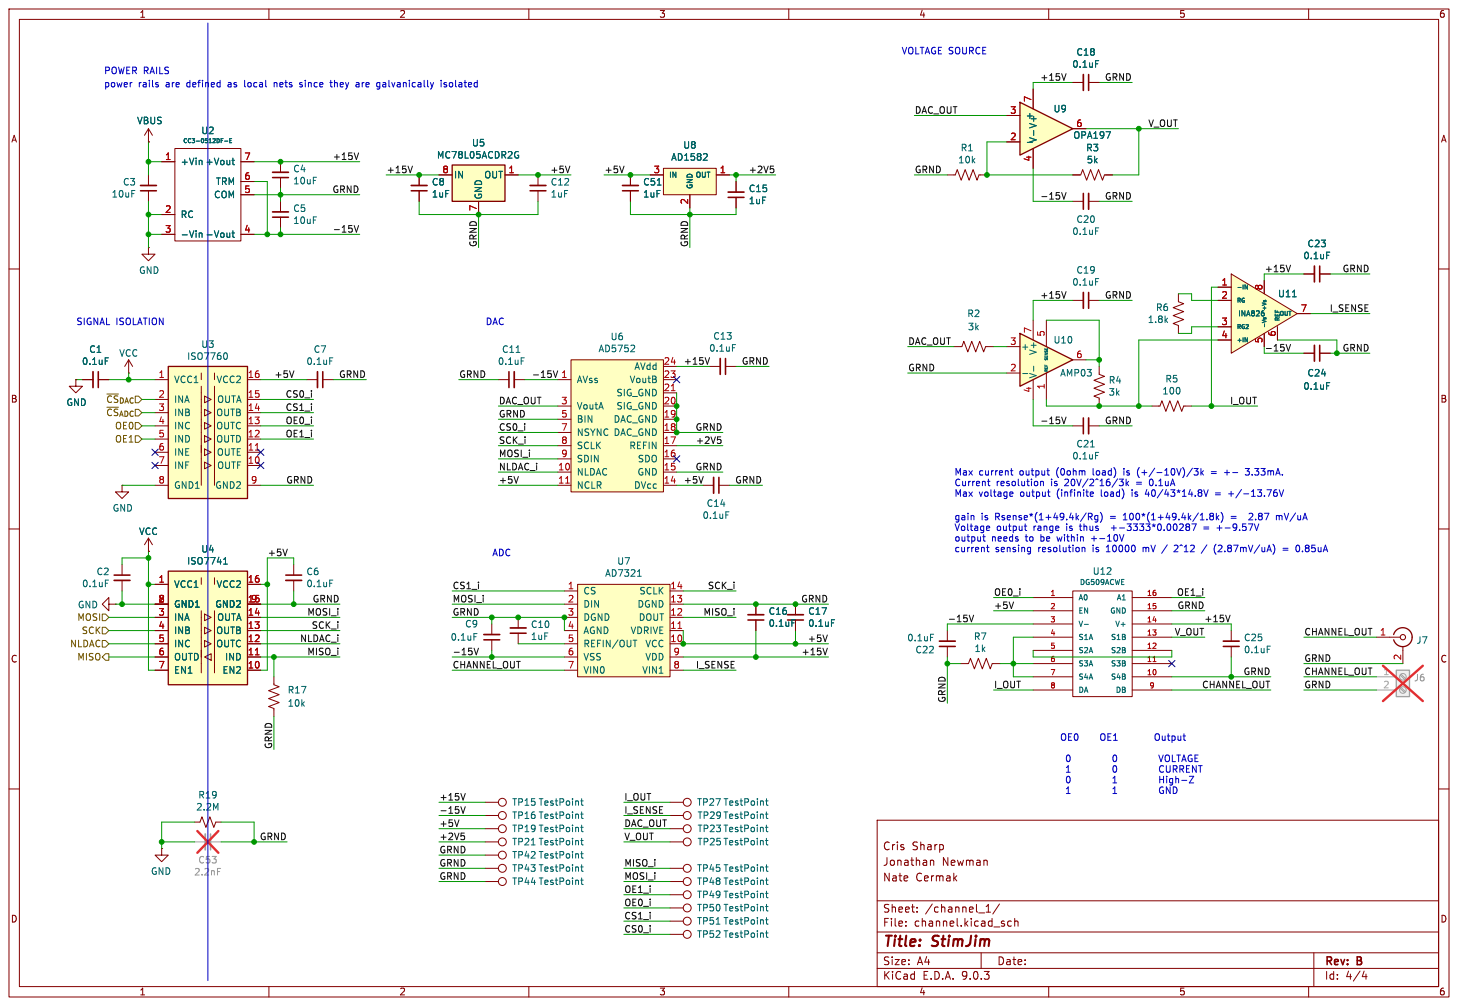
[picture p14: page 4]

output needs to be within +-10V

File: channel.kicad_sch Sheet: /channel_1/ Nate Cermak

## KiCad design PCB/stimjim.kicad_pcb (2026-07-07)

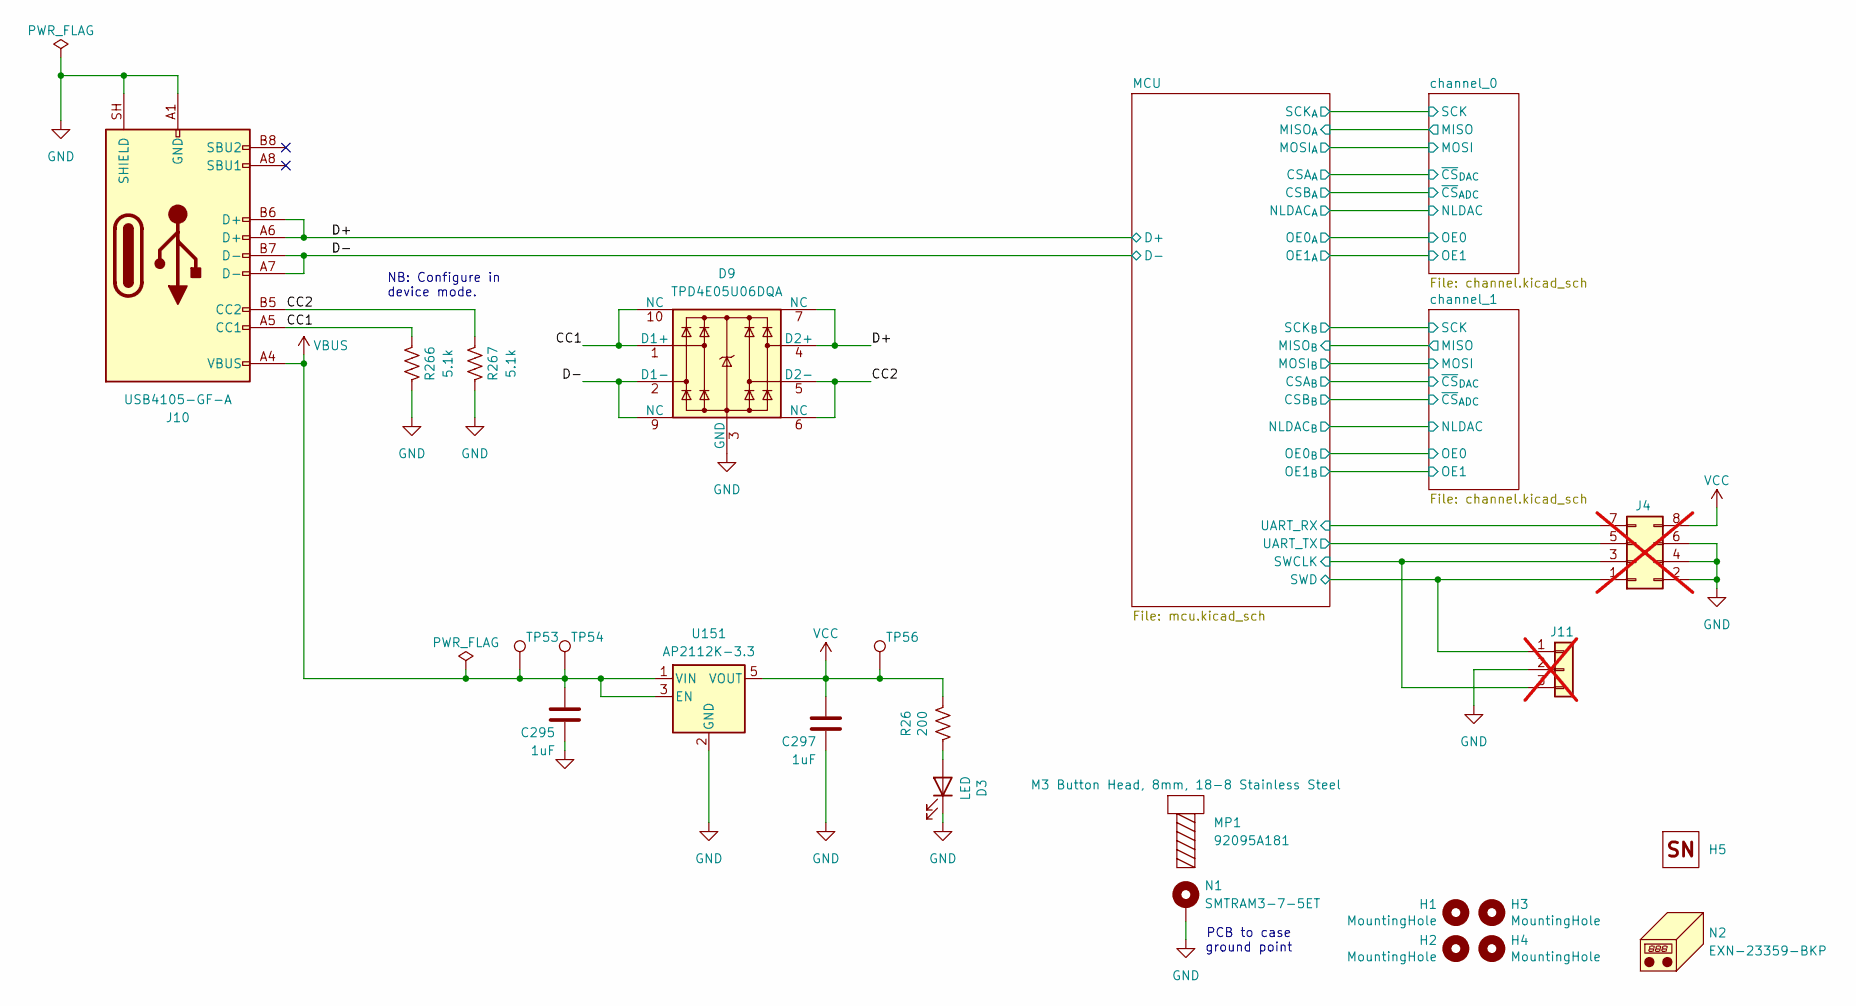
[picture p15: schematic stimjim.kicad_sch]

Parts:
C295, C297: 1uF; C_0603_1608Metric; Voltage 25V; MPN CL10A105KA8NNNC
D3: LED; LUMEX_SSF-LHXH100GD-01; MPN SSF-LXH100GD-01
D9: TPD4E05U06DQA; USON-10_2.5x1.0mm_P0.5mm; MPN TPD4E05U06DQAR
H1, H2, H3, H4: MountingHole; MountingHole_4.3mm_M4
H5: OEPS_SN-STICKER-8x20mm
J4: 10129383-910002ALF; PinHeader_2x04_P2.54mm_Vertical_SMD; MPN 10129383-910002ALF; not fitted
J10: USB4105-GF-A; USB_C_Receptacle_GCT_USB4105-xx-A_16P_TopMnt_Horizontal; MPN USB4105-GF-A
J11: BM03B-SRSS-TB; JST_SH_BM03B-SRSS-TB_1x03-1MP_P1.00mm_Vertical; MPN BM03B-SRSS-TB; not fitted
MP1: 92095A181
N1: SMTRAM3-7-5ET; SMTRA_M3-7-5ET; MPN SMTRAM3-7-5ET
N2: EXN-23359-BKP; MPN EXN-23359-SVP
R26: 200; R_0603_1608Metric; MPN RC0603FR-07200RL
R266, R267: 5.1k; R_0402_1005Metric; Tolerance 1%; MPN ERJ-2RKF5101X
TP53, TP54: GND; TestPoint_Pad_D2.0mm
TP56: VCC; TestPoint_Pad_D2.0mm
U151: AP2112K-3.3; SOT-23-5; MPN AP2112K-3.3TRG1

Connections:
/CC1: D9.1 (D1+), D9.10 (NC), J10.A5 (CC1), R266.1
/CC2: D9.5 (D2-), D9.6 (NC), J10.B5 (CC2), R267.1
/D+: D9.4 (D2+), D9.7 (NC), J10.A6 (D+), J10.B6 (D+); also elsewhere on the board
/D-: D9.2 (D1-), D9.9 (NC), J10.A7 (D-), J10.B7 (D-); also elsewhere on the board
/MCU/SWCLK: J4.3, J11.3; also elsewhere on the board
/MCU/SWD: J4.1, J11.1; also elsewhere on the board
/MCU/UART_RX: J4.7; also elsewhere on the board
/MCU/UART_TX: J4.5; also elsewhere on the board
GND: C295.2, C297.2, D3.1 (K), D9.3 (GND), D9.8 (GND), J4.2, J4.4, J4.6, J10.A1 (GND), J10.A12 (GND), J10.B1 (GND), J10.B12 (GND), J10.SH (SHIELD), J11.2, N1.1 (1_1), R266.2, R267.2, U151.2 (GND); also elsewhere on the board
unnamed: D3.2 (A), R26.2
VBUS: C295.1, J10.A4 (VBUS), J10.A9 (VBUS), J10.B4 (VBUS), J10.B9 (VBUS), TP53.1 (1_1), TP54.1 (1_1), U151.1 (VIN), U151.3 (EN); also elsewhere on the board
VCC: C297.1, J4.8, R26.1, TP56.1 (1_1), U151.5 (VOUT); also elsewhere on the board

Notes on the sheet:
NB: Configure in device mode.
PCB to case ground point

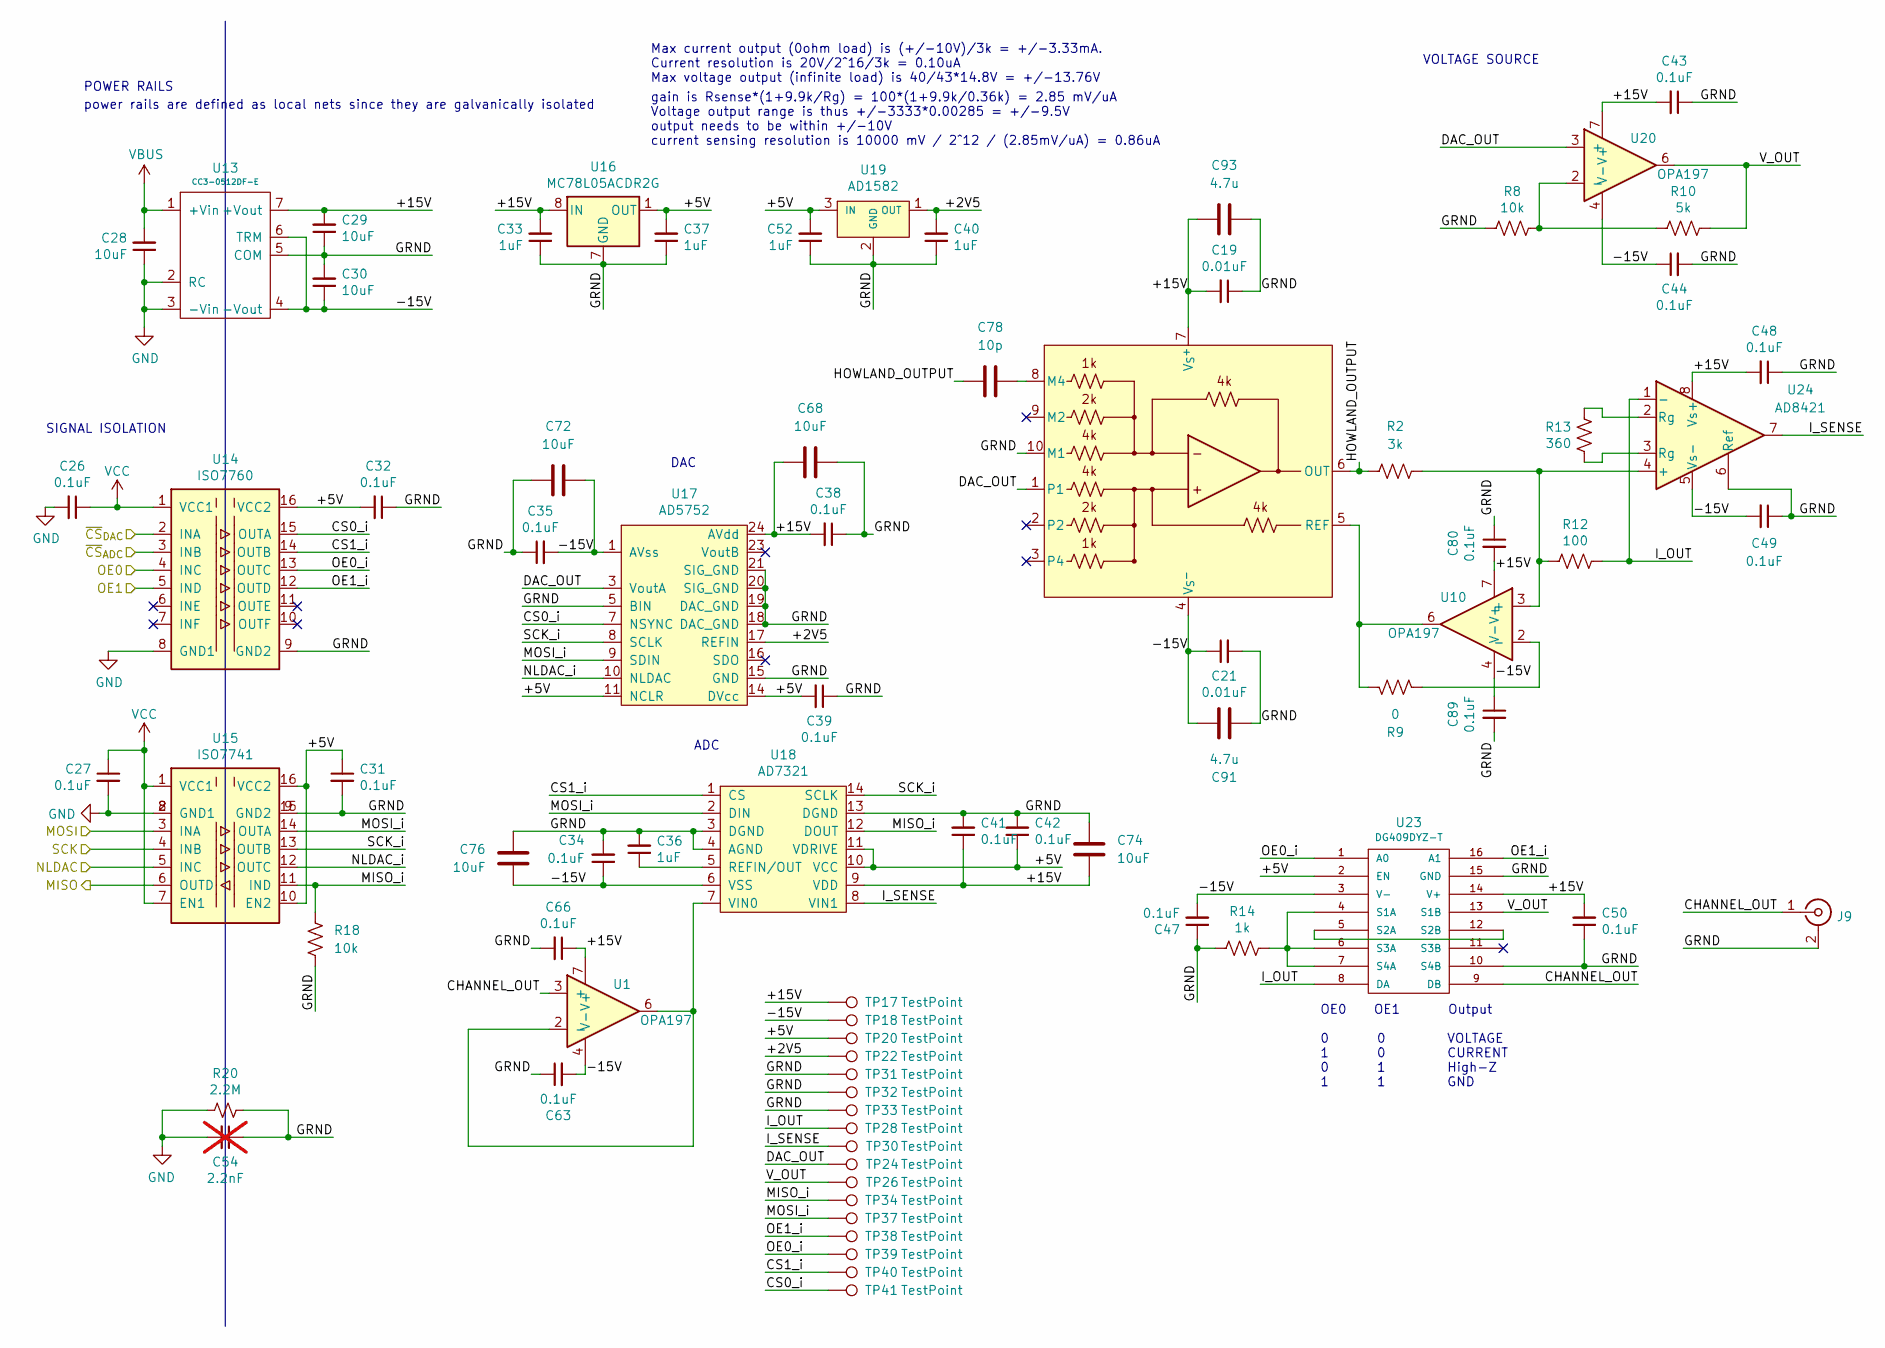
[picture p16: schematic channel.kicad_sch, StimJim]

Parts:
C19, C21: 0.01uF; C_0603_1608Metric; MPN C1608X7R1H103K080AA
C26, C27, C31, C32, C34, C35, C38, C39, C41, C42, C43, C44, C47, C48, C49, C50, C63, C66, C80, C89: 0.1uF; C_0603_1608Metric; MPN GRM188R72A104KA35D
C28, C29, C30: 10uF; C_1206_3216Metric_Pad1.33x1.80mm_HandSolder; Voltage 25V; MPN GRT319R6YA106KE01D
C33, C36, C37, C40, C52: 1uF; C_0603_1608Metric; Voltage 25V; MPN CL10A105KA8NNNC
C54: 2.2nF; C_1210_3225Metric_Pad1.33x2.70mm_HandSolder; MPN DNP; not fitted
C68, C72, C74, C76: 10uF; C_0603_1608Metric; MPN GRM188R6YA106MA73J
C78: 10p; C_0603_1608Metric; MPN C0603C100J5GACTU
C91, C93: 4.7u; C_0603_1608Metric; MPN GRM188R61E475KE11D
J9: 0731375003; BNC_Amphenol_B6252HB-NPP3G-50_Horizontal; MPN 0731375003
R2: 3k; R_0603_1608Metric; Tolerance 1%; MPN RG1608P-302-B-T5
R8: 10k; R_0603_1608Metric; Tolerance 0.1%; MPN RG1608P-103-B-T5
R9: 0; R_0603_1608Metric; MPN RCS06030000Z0EA
R10: 5k; R_0603_1608Metric; Tolerance 0.1%; MPN RG1608P-4991-B-T5
R12: 100; R_0603_1608Metric; Tolerance 0.1%; MPN RG1608P-101-B-T5
R13: 360; R_0603_1608Metric; Tolerance 0.1%; MPN RG1608P-361-B-T5
R14: 1k; R_0603_1608Metric; Tolerance 1%; MPN RG1608P-102-B-T5
R18: 10k; R_0603_1608Metric; MPN RC0603FR-0710KL
R20: 2.2M; R_1210_3225Metric_Pad1.30x2.65mm_HandSolder; MPN CRGCQ1210J2M2
TP17, TP18, TP20, TP22: TestPoint; TestPoint_THTPad_1.0x1.0mm_Drill0.5mm
TP24, TP26, TP28, TP30, TP31, TP32, TP33, TP34, TP37, TP38, TP39, TP40, TP41: TestPoint; TestPoint_THTPad_D1.0mm_Drill0.5mm
U1, U10, U20: OPA197; SOIC-8_3.9x4.9mm_P1.27mm; MPN OPA197IDR
U13: CC3-0512DF-E; MPN CC3-0512DF-E
U14: ISO7760; SOIC-16W_7.5x10.3mm_P1.27mm; MPN ISO7760DWR
U15: ISO7741; SOIC-16W_7.5x10.3mm_P1.27mm; MPN ISO7741DWR
U16: MC78L05ACDR2G; SOIC-8_3.9x4.9mm_P1.27mm; MPN MC78L05ACDR2G
U17: AD5752; TSSOP-24_4.4x7.8mm_P0.65mm; MPN AD5752AREZ
U18: AD7321; TSSOP-14_4.4x5mm_P0.65mm; MPN AD7321BRUZ-REEL7
U19: AD1582; SOT-23; MPN AD1582ARTZ-REEL7
U23: DG409DYZ-T; SO-16_3.9x9.9mm_P1.27mm; MPN DG409DYZ-T
U24: AD8421; SOIC-8_3.9x4.9mm_P1.27mm; MPN AD8421BRZ-R7
U27: LT1995; MSOP-10_3x3mm_P0.5mm; MPN LT1995CMS#PBF

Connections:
/MCU/CSA_{A}: U14.2 (INA); also elsewhere on the board
/MCU/CSB_{A}: U14.3 (INB); also elsewhere on the board
/MCU/MISO_{A}: U15.6 (OUTD); also elsewhere on the board
/MCU/MOSI_{A}: U15.3 (INA); also elsewhere on the board
/MCU/NLDAC_{A}: U15.5 (INC); also elsewhere on the board
/MCU/OE0_{A}: U14.4 (INC); also elsewhere on the board
/MCU/OE1_{A}: U14.5 (IND); also elsewhere on the board
/MCU/SCK_{A}: U15.4 (INB); also elsewhere on the board
/channel_0/+2V5: C40.2, TP22.1 (1_1), U17.17 (REFIN), U19.1 (OUT)
/channel_0/+5V: C31.1, C32.2, C37.2, C39.2, C42.1, C52.2, TP20.1 (1_1), U14.16 (VCC2), U15.10 (EN2), U15.16 (VCC2), U16.1 (OUT), U17.11 (NCLR), U17.14 (DVcc), U18.10 (VCC), U18.11 (VDRIVE), U19.3 (IN), U23.2 (EN)
/channel_0/+15V: C19.2, C29.2, C33.2, C38.2, C41.1, C43.2, C48.2, C50.2, C66.1, C68.1, C74.1, C80.2, C93.2, TP17.1 (1_1), U1.7 (V+), U10.7 (V+), U13.7 (+Vout), U16.8 (IN), U17.24 (AVdd), U18.9 (VDD), U20.7 (V+), U23.14 (V+), U24.8 (Vs+), U27.7 (V_{S}^{+})
/channel_0/-15V: C21.1, C30.1, C34.1, C35.2, C44.1, C47.2, C49.2, C63.2, C72.2, C76.2, C89.1, C91.2, TP18.1 (1_1), U1.4 (V-), U10.4 (V-), U13.4 (-Vout), U13.6 (TRM), U17.1 (AVss), U18.6 (VSS), U20.4 (V-), U23.3 (V-), U24.5 (Vs-), U27.4 (V_{S}^{-})
/channel_0/CHANNEL_OUT: J9.1 (In), U1.3 (+), U23.9 (DB)
/channel_0/CS0_i: TP41.1 (1_1), U14.15 (OUTA), U17.7 (NSYNC)
/channel_0/CS1_i: TP40.1 (1_1), U14.14 (OUTB), U18.1 (CS)
/channel_0/DAC_OUT: TP24.1 (1_1), U17.3 (VoutA), U20.3 (+), U27.1
/channel_0/GRND: C19.1, C21.2, C29.1, C30.2, C31.2, C32.1, C33.1, C34.2, C35.1, C36.2, C37.1, C38.1, C39.1, C40.1, C41.2, C42.2, C43.1, C44.2, C47.1, C48.1, C49.1, C50.1, C52.1, C54.1, C63.1, C66.2, C68.2, C72.1, C74.2, C76.1, C80.1, C89.2, C91.1, C93.1, J9.2 (Ext), R8.1, R14.1, R18.1, R20.1, TP31.1 (1_1), TP32.1 (1_1), TP33.1 (1_1), U13.5 (COM), U14.9 (GND2), U15.9 (GND2), U15.15 (GND2), U16.2 (GND), U16.3 (GND), U16.6 (GND), U16.7 (GND), U17.5 (BIN), U17.15 (GND), U17.18 (DAC_GND), U17.19 (DAC_GND), U17.20 (SIG_GND), U17.21 (SIG_GND), U18.3 (DGND), U18.4 (AGND), U18.13 (DGND), U19.2 (GND), U23.10 (S4B), U23.15 (GND), U24.6 (Ref), U27.10 (M1)
/channel_0/HOWLAND_OUTPUT: C78.1, R2.1, U27.6 (OUT)
/channel_0/I_OUT: R12.2, TP28.1 (1_1), U23.8 (DA), U24.1 (-)
/channel_0/I_SENSE: TP30.1 (1_1), U18.8 (VIN1), U24.7
/channel_0/MISO_i: R18.2, TP34.1 (1_1), U15.11 (IND), U18.12 (DOUT)
/channel_0/MOSI_i: TP37.1 (1_1), U15.14 (OUTA), U17.9 (SDIN), U18.2 (DIN)
/channel_0/NLDAC_i: U15.12 (OUTC), U17.10 (NLDAC)
/channel_0/OE0_i: TP39.1 (1_1), U14.13 (OUTC), U23.1 (A0)
/channel_0/OE1_i: TP38.1 (1_1), U14.12 (OUTD), U23.16 (A1)
/channel_0/SCK_i: U15.13 (OUTB), U17.8 (SCLK), U18.14 (SCLK)
/channel_0/V_OUT: R10.2, TP26.1 (1_1), U20.6, U23.13 (S1B)
GND: C26.2, C27.2, C28.1, C54.2, R20.2, U13.2 (RC), U13.3 (-Vin), U14.8 (GND1), U15.2 (GND1), U15.8 (GND1); also elsewhere on the board
unnamed: R13.1, U24.3 (Rg)
unnamed: R13.2, U24.2 (Rg)
unnamed: U1.2 (-), U1.6, U18.7 (VIN0)
unnamed: R2.2, R12.1, U10.3 (+), U24.4 (+)
unnamed: R9.2, U10.2 (-)
unnamed: C36.1, U18.5 (REFIN/OUT)
unnamed: R8.2, R10.1, U20.2 (-)
unnamed: R14.2, U23.4 (S1A), U23.6 (S3A), U23.7 (S4A)
unnamed: U23.5 (S2A), U23.12 (S2B)
unnamed: C78.2, U27.8 (M4)
unnamed: R9.1, U10.6, U27.5 (REF)
VBUS: C28.2, U13.1 (+Vin); also elsewhere on the board
VCC: C26.1, C27.1, U14.1 (VCC1), U15.1 (VCC1), U15.7 (EN1); also elsewhere on the board

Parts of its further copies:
C1, C2, C6, C7, C9, C11, C13, C14, C16, C17, C18, C20, C22, C23, C24, C25, C65, C67, C82, C90: 0.1uF; C_0603_1608Metric; MPN GRM188R72A104KA35D
C3, C4, C5: 10uF; C_1206_3216Metric_Pad1.33x1.80mm_HandSolder; Voltage 25V; MPN GRT319R6YA106KE01D
C8, C10, C12, C15, C51: 1uF; C_0603_1608Metric; Voltage 25V; MPN CL10A105KA8NNNC
C45, C46: 0.01uF; C_0603_1608Metric; MPN C1608X7R1H103K080AA
C53: 2.2nF; C_1210_3225Metric_Pad1.33x2.70mm_HandSolder; MPN DNP; not fitted
C69, C73, C75, C77: 10uF; C_0603_1608Metric; MPN GRM188R6YA106MA73J
C79: 10p; C_0603_1608Metric; MPN C0603C100J5GACTU
C92, C94: 4.7u; C_0603_1608Metric; MPN GRM188R61E475KE11D
J7: 0731375003; BNC_Amphenol_B6252HB-NPP3G-50_Horizontal; MPN 0731375003
R1: 10k; R_0603_1608Metric; Tolerance 0.1%; MPN RG1608P-103-B-T5
R3: 5k; R_0603_1608Metric; Tolerance 0.1%; MPN RG1608P-4991-B-T5
R4: 3k; R_0603_1608Metric; Tolerance 1%; MPN RG1608P-302-B-T5
R5: 100; R_0603_1608Metric; Tolerance 0.1%; MPN RG1608P-101-B-T5
R6: 360; R_0603_1608Metric; Tolerance 0.1%; MPN RG1608P-361-B-T5
R7: 1k; R_0603_1608Metric; Tolerance 1%; MPN RG1608P-102-B-T5
R11: 0; R_0603_1608Metric; MPN RCS06030000Z0EA
R17: 10k; R_0603_1608Metric; MPN RC0603FR-0710KL
R19: 2.2M; R_1210_3225Metric_Pad1.30x2.65mm_HandSolder; MPN CRGCQ1210J2M2
TP15, TP16, TP19, TP21: TestPoint; TestPoint_THTPad_1.0x1.0mm_Drill0.5mm
TP23, TP25, TP27, TP29, TP42, TP43, TP44, TP45, TP48, TP49, TP50, TP51, TP52: TestPoint; TestPoint_THTPad_D1.0mm_Drill0.5mm
U2: CC3-0512DF-E; MPN CC3-0512DF-E
U3: ISO7760; SOIC-16W_7.5x10.3mm_P1.27mm; MPN ISO7760DWR
U4: ISO7741; SOIC-16W_7.5x10.3mm_P1.27mm; MPN ISO7741DWR
U5: MC78L05ACDR2G; SOIC-8_3.9x4.9mm_P1.27mm; MPN MC78L05ACDR2G
U6: AD5752; TSSOP-24_4.4x7.8mm_P0.65mm; MPN AD5752AREZ
U7: AD7321; TSSOP-14_4.4x5mm_P0.65mm; MPN AD7321BRUZ-REEL7
U8: AD1582; SOT-23; MPN AD1582ARTZ-REEL7
U9, U21, U26: OPA197; SOIC-8_3.9x4.9mm_P1.27mm; MPN OPA197IDR
U12: DG409DYZ-T; SO-16_3.9x9.9mm_P1.27mm; MPN DG409DYZ-T
U28: LT1995; MSOP-10_3x3mm_P0.5mm; MPN LT1995CMS#PBF
U29: AD8421; SOIC-8_3.9x4.9mm_P1.27mm; MPN AD8421BRZ-R7

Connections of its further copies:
/MCU/CSA_{B}: U3.2 (INA); also elsewhere on the board
/MCU/CSB_{B}: U3.3 (INB); also elsewhere on the board
/MCU/MISO_{B}: U4.6 (OUTD); also elsewhere on the board
/MCU/MOSI_{B}: U4.3 (INA); also elsewhere on the board
/MCU/NLDAC_{B}: U4.5 (INC); also elsewhere on the board
/MCU/OE0_{B}: U3.4 (INC); also elsewhere on the board
/MCU/OE1_{B}: U3.5 (IND); also elsewhere on the board
/MCU/SCK_{B}: U4.4 (INB); also elsewhere on the board
/channel_1/+2V5: C15.2, TP21.1 (1_1), U6.17 (REFIN), U8.1 (OUT)
/channel_1/+5V: C6.1, C7.2, C12.2, C14.2, C17.1, C51.2, TP19.1 (1_1), U3.16 (VCC2), U4.10 (EN2), U4.16 (VCC2), U5.1 (OUT), U6.11 (NCLR), U6.14 (DVcc), U7.10 (VCC), U7.11 (VDRIVE), U8.3 (IN), U12.2 (EN)
/channel_1/+15V: C4.2, C8.2, C13.2, C16.1, C18.2, C23.2, C25.2, C45.2, C67.1, C69.1, C75.1, C82.2, C94.2, TP15.1 (1_1), U2.7 (+Vout), U5.8 (IN), U6.24 (AVdd), U7.9 (VDD), U9.7 (V+), U12.14 (V+), U21.7 (V+), U26.7 (V+), U28.7 (V_{S}^{+}), U29.8 (Vs+)
/channel_1/-15V: C5.1, C9.1, C11.2, C20.1, C22.2, C24.2, C46.1, C65.2, C73.2, C77.2, C90.1, C92.2, TP16.1 (1_1), U2.4 (-Vout), U2.6 (TRM), U6.1 (AVss), U7.6 (VSS), U9.4 (V-), U12.3 (V-), U21.4 (V-), U26.4 (V-), U28.4 (V_{S}^{-}), U29.5 (Vs-)
/channel_1/CHANNEL_OUT: J7.1 (In), U12.9 (DB), U26.3 (+)
/channel_1/CS0_i: TP52.1 (1_1), U3.15 (OUTA), U6.7 (NSYNC)
/channel_1/CS1_i: TP51.1 (1_1), U3.14 (OUTB), U7.1 (CS)
/channel_1/DAC_OUT: TP23.1 (1_1), U6.3 (VoutA), U9.3 (+), U28.1
/channel_1/GRND: C4.1, C5.2, C6.2, C7.1, C8.1, C9.2, C10.2, C11.1, C12.1, C13.1, C14.1, C15.1, C16.2, C17.2, C18.1, C20.2, C22.1, C23.1, C24.1, C25.1, C45.1, C46.2, C51.1, C53.1, C65.1, C67.2, C69.2, C73.1, C75.2, C77.1, C82.1, C90.2, C92.1, C94.1, J7.2 (Ext), R1.1, R7.1, R17.1, R19.1, TP42.1 (1_1), TP43.1 (1_1), TP44.1 (1_1), U2.5 (COM), U3.9 (GND2), U4.9 (GND2), U4.15 (GND2), U5.2 (GND), U5.3 (GND), U5.6 (GND), U5.7 (GND), U6.5 (BIN), U6.15 (GND), U6.18 (DAC_GND), U6.19 (DAC_GND), U6.20 (SIG_GND), U6.21 (SIG_GND), U7.3 (DGND), U7.4 (AGND), U7.13 (DGND), U8.2 (GND), U12.10 (S4B), U12.15 (GND), U28.10 (M1), U29.6 (Ref)
/channel_1/HOWLAND_OUTPUT: C79.1, R4.1, U28.6 (OUT)
/channel_1/I_OUT: R5.2, TP27.1 (1_1), U12.8 (DA), U29.1 (-)
/channel_1/I_SENSE: TP29.1 (1_1), U7.8 (VIN1), U29.7
/channel_1/MISO_i: R17.2, TP45.1 (1_1), U4.11 (IND), U7.12 (DOUT)
/channel_1/MOSI_i: TP48.1 (1_1), U4.14 (OUTA), U6.9 (SDIN), U7.2 (DIN)
/channel_1/NLDAC_i: U4.12 (OUTC), U6.10 (NLDAC)
/channel_1/OE0_i: TP50.1 (1_1), U3.13 (OUTC), U12.1 (A0)
/channel_1/OE1_i: TP49.1 (1_1), U3.12 (OUTD), U12.16 (A1)
/channel_1/SCK_i: U4.13 (OUTB), U6.8 (SCLK), U7.14 (SCLK)
/channel_1/V_OUT: R3.2, TP25.1 (1_1), U9.6, U12.13 (S1B)
GND: C1.2, C2.2, C3.1, C53.2, R19.2, U2.2 (RC), U2.3 (-Vin), U3.8 (GND1), U4.2 (GND1), U4.8 (GND1); also elsewhere on the board
unnamed: R6.1, U29.3 (Rg)
unnamed: R6.2, U29.2 (Rg)
unnamed: C10.1, U7.5 (REFIN/OUT)
unnamed: R1.2, R3.1, U9.2 (-)
unnamed: R7.2, U12.4 (S1A), U12.6 (S3A), U12.7 (S4A)
unnamed: U12.5 (S2A), U12.12 (S2B)
unnamed: R4.2, R5.1, U21.3 (+), U29.4 (+)
unnamed: R11.2, U21.2 (-)
unnamed: U7.7 (VIN0), U26.2 (-), U26.6
unnamed: C79.2, U28.8 (M4)
unnamed: R11.1, U21.6, U28.5 (REF)
VBUS: C3.2, U2.1 (+Vin); also elsewhere on the board
VCC: C1.1, C2.1, U3.1 (VCC1), U4.1 (VCC1), U4.7 (EN1); also elsewhere on the board

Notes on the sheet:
power rails are defined as local nets since they are galvanically isolated
ADC
gain is Rsense*(1+9.9k/Rg) = 100*(1+9.9k/0.36k) = 2.85 mV/uA Voltage output range is thus +/-3333*0.00285 = +/-9.5V output needs to be within +/-10V current sensing resolution is 10000 mV / 2^12 / (2.85mV/uA) = 0.86uA
OE0 OE1 Output 0 0 VOLTAGE 1 0 CURRENT 0 1 High-Z 1 1 GND
SIGNAL ISOLATION
POWER RAILS
VOLTAGE SOURCE
DAC
Max current output (0ohm load) is (+/-10V)/3k = +/-3.33mA. Current resolution is 20V/2^16/3k = 0.10uA Max voltage output (infinite load) is 40/43*14.8V = +/-13.76V

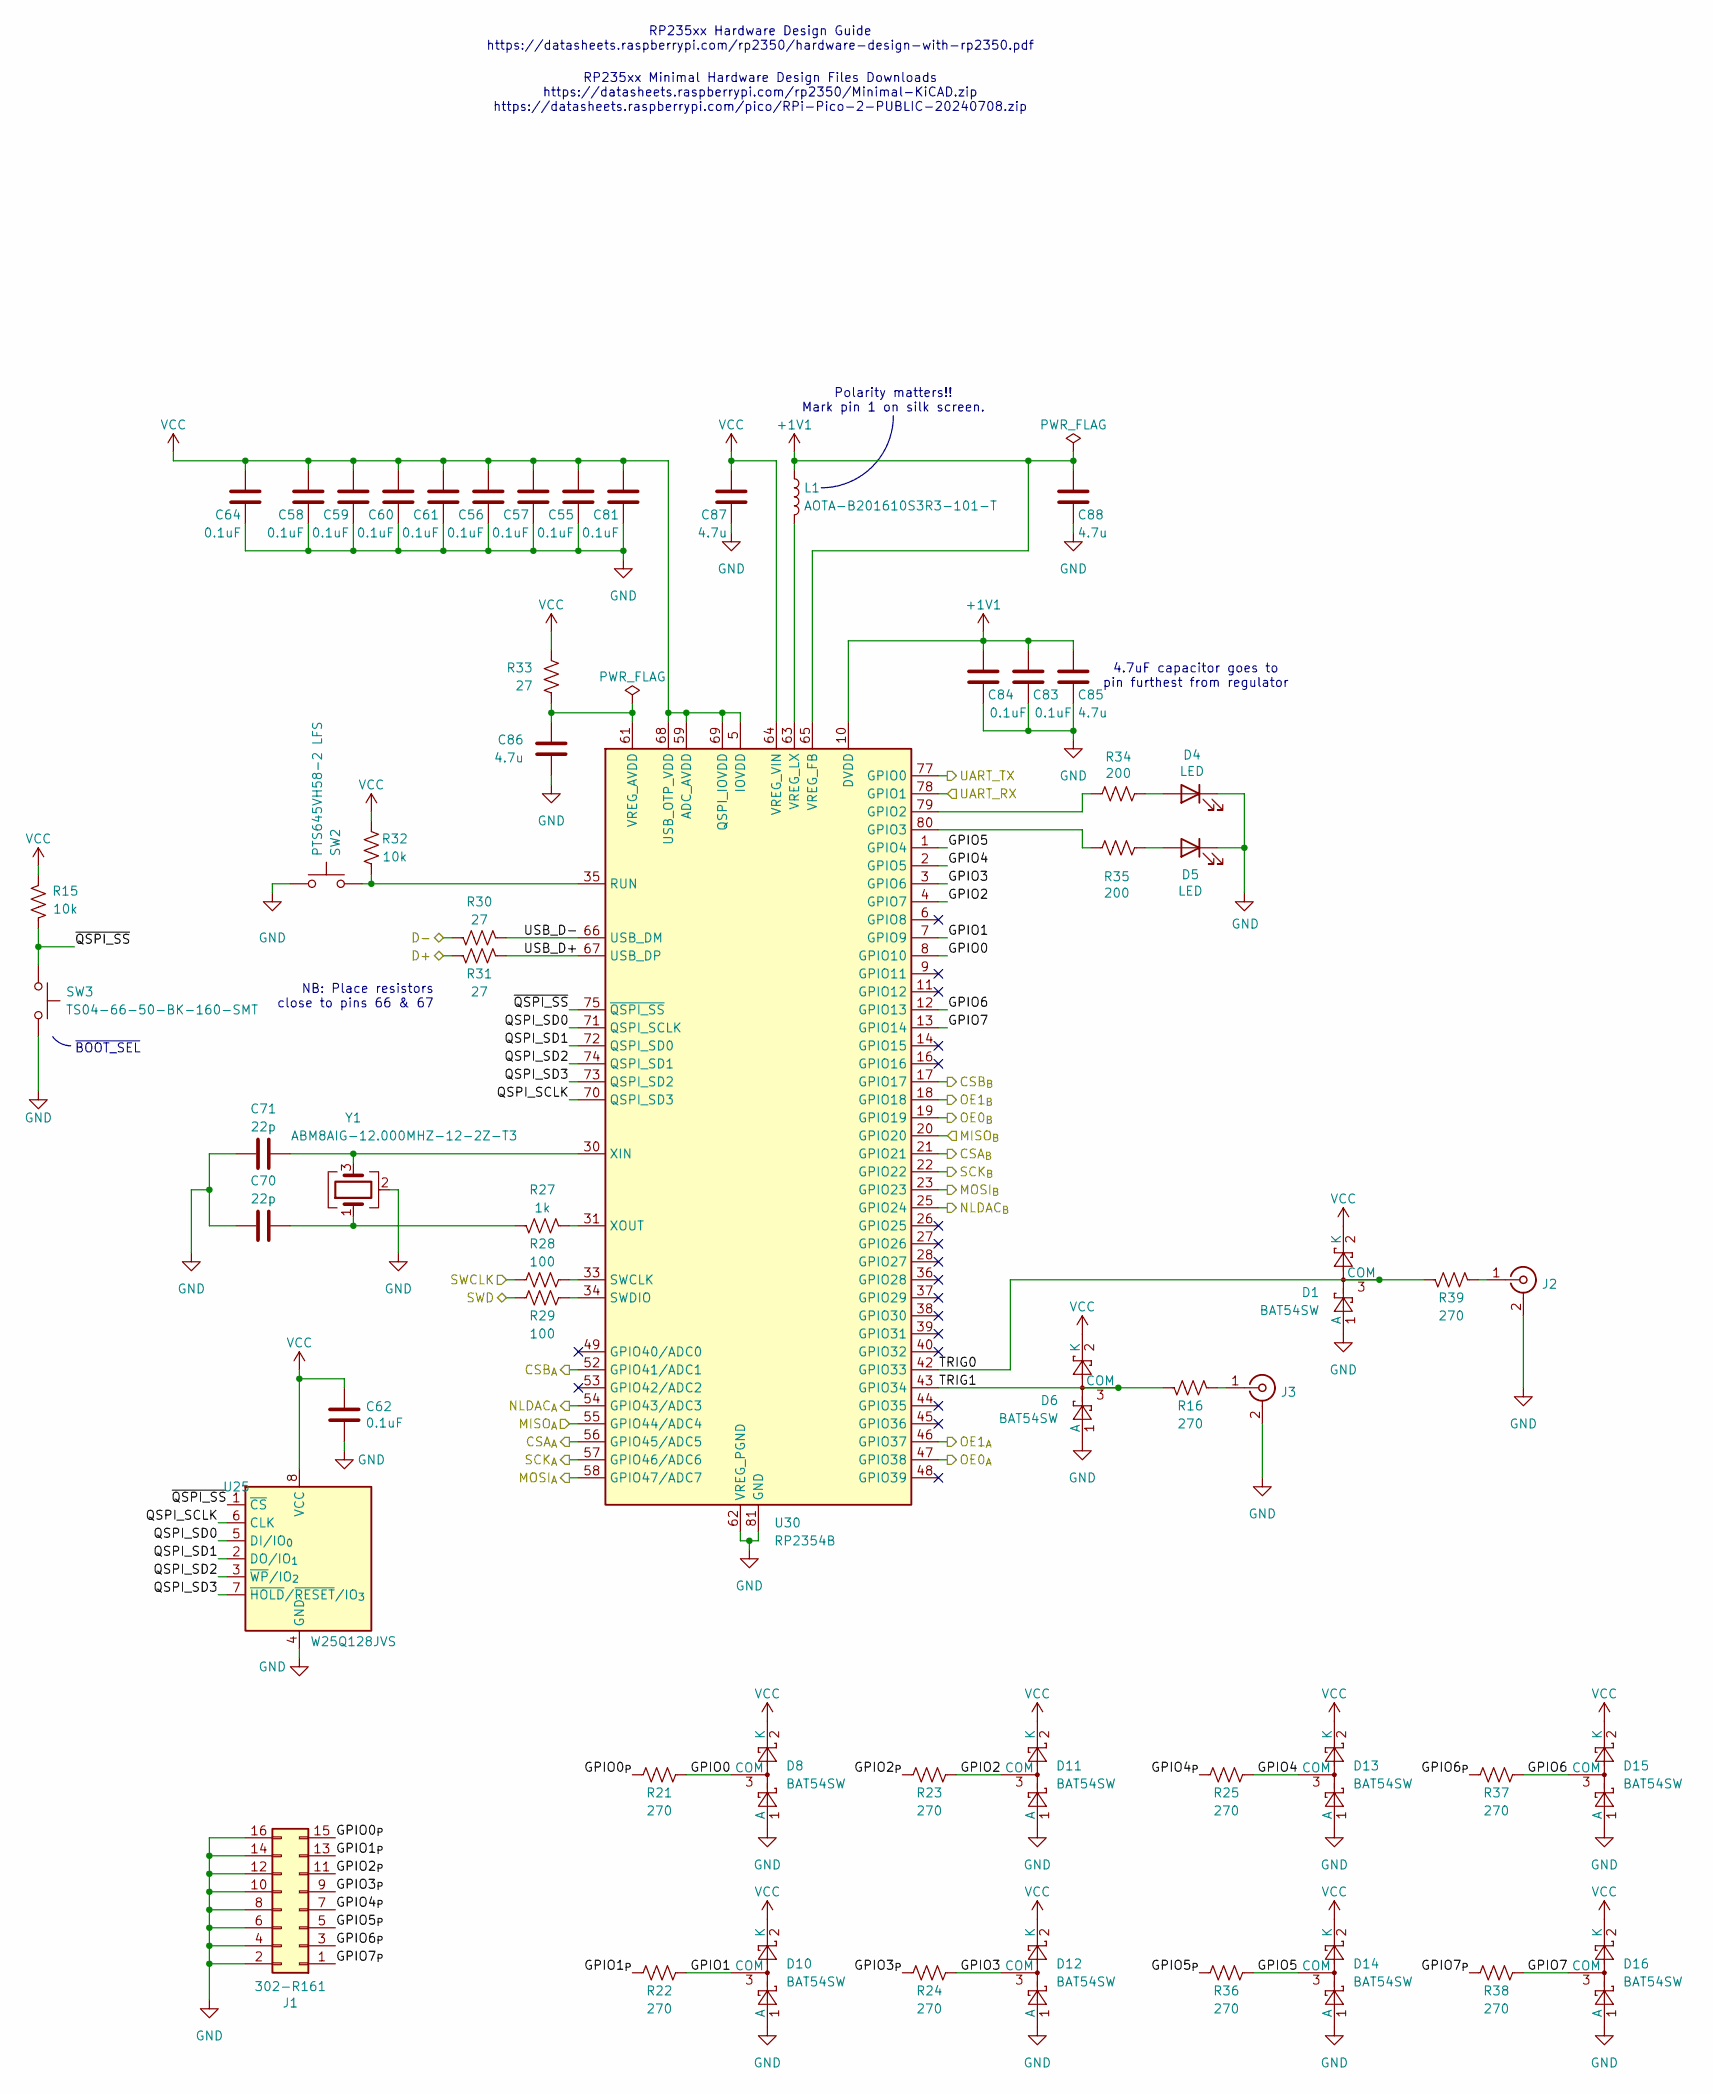
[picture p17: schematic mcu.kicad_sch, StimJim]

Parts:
C55, C56, C57, C58, C59, C60, C61, C62, C64, C81, C83, C84: 0.1uF; C_0402_1005Metric; MPN C1005X7R1E104K050BB
C70, C71: 22p; C_0402_1005Metric; MPN CL05C220JB51PNC
C85, C86, C87, C88: 4.7u; C_0402_1005Metric; Voltage 16V; MPN KGM05CR51C475MH
D1, D6, D8, D10, D11, D12, D13, D14, D15, D16: BAT54SW; SOT-323_SC-70; MPN BAT54SW
D4, D5: LED; LUMEX_SSF-LHXH100GD-01; MPN SSF-LXH100GD-01
J1: 302-R161; IDC-Header_2x08_P2.54mm_Horizontal; MPN 302-R161
J2, J3: 0731375003; BNC_Amphenol_B6252HB-NPP3G-50_Horizontal; MPN 0731375003
L1: AOTA-B201610S3R3-101-T; L_Abracon_2x1.6x1.0mm; MPN AOTA-B201610S3R3-101-T
R15, R32: 10k; R_0603_1608Metric; MPN RC0603FR-0710KL
R16, R21, R22, R23, R24, R25, R36, R37, R38, R39: 270; R_0805_2012Metric; MPN CRCW0805270RFKEAHP; LCSC C3013376
R27: 1k; R_0603_1608Metric; Tolerance 1%; MPN RG1608P-102-B-T5
R28, R29: 100; R_0603_1608Metric; Tolerance 1%; MPN CRCW0603100RFKEAHP
R30, R31, R33: 27; R_0402_1005Metric; MPN RMCF0402FT27R0
R34, R35: 200; R_0603_1608Metric; MPN RC0603FR-07200RL
SW2: PTS645VH58-2 LFS; SW_Tactile_SPST_Angled_PTS645Vx58-2LFS; MPN PTS645VH58-2 LFS
SW3: TS04-66-50-BK-160-SMT; SAMESKY_TS04-66-XX-BK-XXX-SMT-XX; MPN TS04-66-50-BK-160-SMT
U25: W25Q128JVS; SOIC-8_5.3x5.3mm_P1.27mm; MPN W25Q128JVSIQ
U30: RP2354B; QFN-80-1EP_10x10mm_P0.4mm_EP3.4x3.4mm; MPN SC1512-A4
Y1: ABM8AIG-12.000MHZ-12-2Z-T3; Crystal_SMD_Abracon_ABM8AIG-4Pin_3.2x2.5mm; MPN ABM8AIG-12.000MHZ-12-2Z-T3

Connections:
+1V1: C83.1, C84.1, C85.1, C88.1, L1.1, U30.10 (DVDD), U30.32 (DVDD), U30.51 (DVDD), U30.65 (VREG_FB)
/D+: R31.2; also elsewhere on the board
/D-: R30.2; also elsewhere on the board
/MCU/CSA_{A}: U30.56 (GPIO45/ADC5); also elsewhere on the board
/MCU/CSA_{B}: U30.21 (GPIO21); also elsewhere on the board
/MCU/CSB_{A}: U30.52 (GPIO41/ADC1); also elsewhere on the board
/MCU/CSB_{B}: U30.17 (GPIO17); also elsewhere on the board
/MCU/GPIO0: D8.3 (COM), R21.2, U30.8 (GPIO10)
/MCU/GPIO0_{P}: J1.15, R21.1
/MCU/GPIO1: D10.3 (COM), R22.2, U30.7 (GPIO9)
/MCU/GPIO1_{P}: J1.13, R22.1
/MCU/GPIO2: D11.3 (COM), R23.2, U30.4 (GPIO7)
/MCU/GPIO2_{P}: J1.11, R23.1
/MCU/GPIO3: D12.3 (COM), R24.2, U30.3 (GPIO6)
/MCU/GPIO3_{P}: J1.9, R24.1
/MCU/GPIO4: D13.3 (COM), R25.2, U30.2 (GPIO5)
/MCU/GPIO4_{P}: J1.7, R25.1
/MCU/GPIO5: D14.3 (COM), R36.2, U30.1 (GPIO4)
/MCU/GPIO5_{P}: J1.5, R36.1
/MCU/GPIO6: D15.3 (COM), R37.2, U30.12 (GPIO13)
/MCU/GPIO6_{P}: J1.3, R37.1
/MCU/GPIO7: D16.3 (COM), R38.2, U30.13 (GPIO14)
/MCU/GPIO7_{P}: J1.1, R38.1
/MCU/MISO_{A}: U30.55 (GPIO44/ADC4); also elsewhere on the board
/MCU/MISO_{B}: U30.20 (GPIO20); also elsewhere on the board
/MCU/MOSI_{A}: U30.58 (GPIO47/ADC7); also elsewhere on the board
/MCU/MOSI_{B}: U30.23 (GPIO23); also elsewhere on the board
/MCU/NLDAC_{A}: U30.54 (GPIO43/ADC3); also elsewhere on the board
/MCU/NLDAC_{B}: U30.25 (GPIO24); also elsewhere on the board
/MCU/OE0_{A}: U30.47 (GPIO38); also elsewhere on the board
/MCU/OE0_{B}: U30.19 (GPIO19); also elsewhere on the board
/MCU/OE1_{A}: U30.46 (GPIO37); also elsewhere on the board
/MCU/OE1_{B}: U30.18 (GPIO18); also elsewhere on the board
/MCU/QSPI_SCLK: U25.6 (CLK), U30.70 (QSPI_SD3)
/MCU/QSPI_SD0: U25.5 (DI/IO_{0}), U30.71 (QSPI_SCLK)
/MCU/QSPI_SD1: U25.2 (DO/IO_{1}), U30.72 (QSPI_SD0)
/MCU/QSPI_SD2: U25.3 (~WP/IO_{2}), U30.74 (QSPI_SD1)
/MCU/QSPI_SD3: U25.7 (~HOLD/~RESET/IO_{3}), U30.73 (QSPI_SD2)
/MCU/SCK_{A}: U30.57 (GPIO46/ADC6); also elsewhere on the board
/MCU/SCK_{B}: U30.22 (GPIO22); also elsewhere on the board
/MCU/SWCLK: R28.1; also elsewhere on the board
/MCU/SWD: R29.1; also elsewhere on the board
/MCU/TRIG0: D1.3 (COM), R39.2, U30.42 (GPIO33)
/MCU/TRIG1: D6.3 (COM), R16.2, U30.43 (GPIO34)
/MCU/UART_RX: U30.78 (GPIO1); also elsewhere on the board
/MCU/UART_TX: U30.77 (GPIO0); also elsewhere on the board
/MCU/USB_D+: R31.1, U30.67 (USB_DP)
/MCU/USB_D-: R30.1, U30.66 (USB_DM)
/MCU/~QSPI_SS: R15.2, SW3.2, U25.1 (~CS), U30.75 (~QSPI_SS)
GND: C55.2, C56.2, C57.2, C58.2, C59.2, C60.2, C61.2, C62.2, C64.2, C70.1, C71.1, C81.2, C83.2, C84.2, C85.2, C86.2, C87.2, C88.2, D1.1 (A), D4.1 (K), D5.1 (K), D6.1 (A), D8.1 (A), D10.1 (A), D11.1 (A), D12.1 (A), D13.1 (A), D14.1 (A), D15.1 (A), D16.1 (A), J1.2, J1.4, J1.6, J1.8, J1.10, J1.12, J1.14, J1.16, J2.2 (Ext), J3.2 (Ext), SW2.1, SW3.1, U25.4 (GND), U30.62 (VREG_PGND), U30.81 (GND), Y1.2 (G), Y1.4 (G); also elsewhere on the board
unnamed: C70.2, R27.2, Y1.1
unnamed: D4.2 (A), R34.1
unnamed: D5.2 (A), R35.1
unnamed: J2.1 (In), R39.1
unnamed: J3.1 (In), R16.1
unnamed: R34.2, U30.79 (GPIO2)
unnamed: R35.2, U30.80 (GPIO3)
unnamed: R32.2, SW2.2, U30.35 (RUN)
unnamed: R28.2, U30.33 (SWCLK)
unnamed: R29.2, U30.34 (SWDIO)
unnamed: C86.1, R33.2, U30.61 (VREG_AVDD)
unnamed: L1.2, U30.63 (VREG_LX)
unnamed: C71.2, U30.30 (XIN), Y1.3
unnamed: R27.1, U30.31 (XOUT)
VCC: C55.1, C56.1, C57.1, C58.1, C59.1, C60.1, C61.1, C62.1, C64.1, C81.1, C87.1, D1.2 (K), D6.2 (K), D8.2 (K), D10.2 (K), D11.2 (K), D12.2 (K), D13.2 (K), D14.2 (K), D15.2 (K), D16.2 (K), R15.1, R32.1, R33.1, U25.8 (VCC), U30.5 (IOVDD), U30.15 (IOVDD), U30.24 (IOVDD), U30.29 (IOVDD), U30.41 (IOVDD), U30.50 (IOVDD), U30.59 (ADC_AVDD), U30.60 (IOVDD), U30.64 (VREG_VIN), U30.68 (USB_OTP_VDD), U30.69 (QSPI_IOVDD), U30.76 (IOVDD); also elsewhere on the board

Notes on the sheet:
Polarity matters!! Mark pin 1 on silk screen.
RP235xx Minimal Hardware Design Files Downloads https://datasheets.raspberrypi.com/rp2350/Minimal-KiCAD.zip https://datasheets.raspberrypi.com/pico/RPi-Pico-2-PUBLIC-20240708.zip
~{BOOT_SEL}
NB: Place resistors close to pins 66 & 67
RP235xx Hardware Design Guide https://datasheets.raspberrypi.com/rp2350/hardware-design-with-rp2350.pdf
4.7uF capacitor goes to pin furthest from regulator

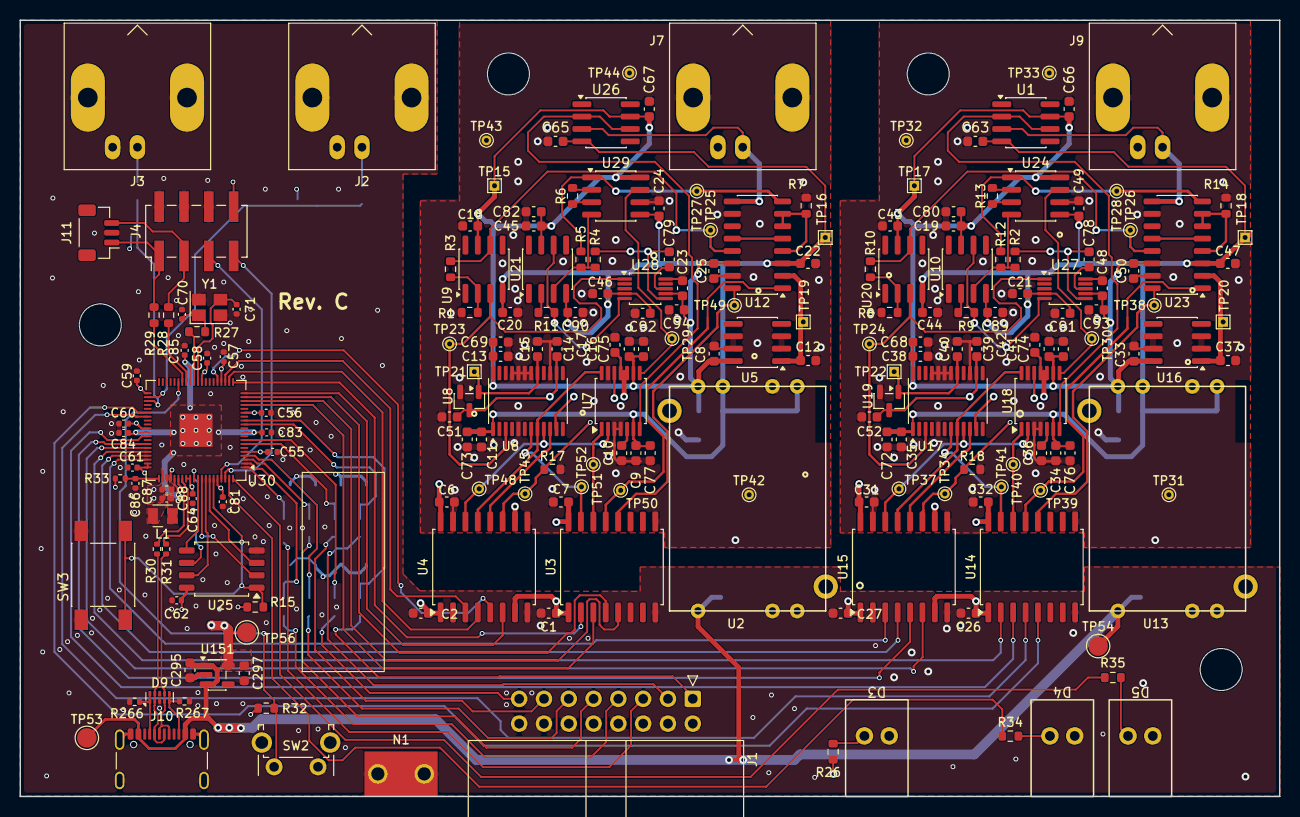
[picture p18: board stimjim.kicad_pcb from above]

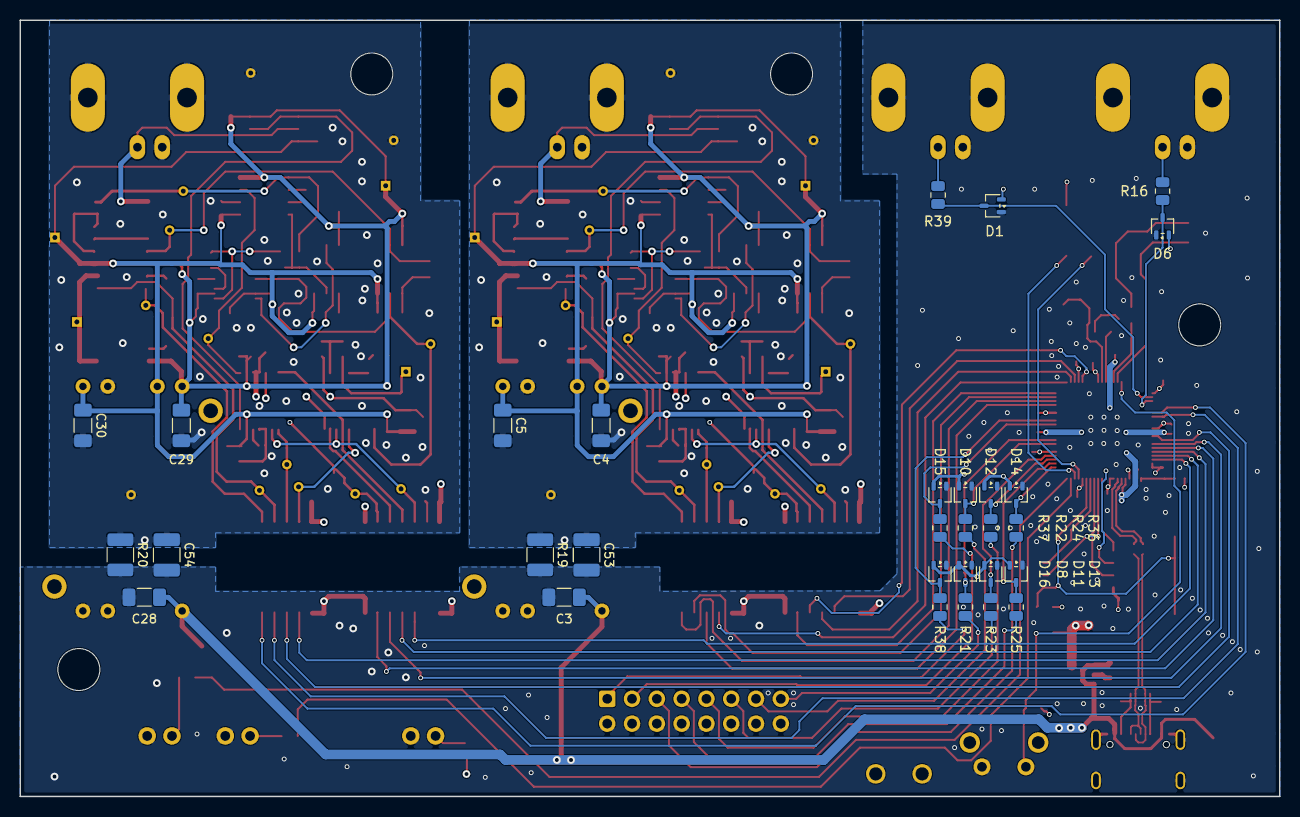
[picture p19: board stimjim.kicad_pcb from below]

Board: 4 copper layers, 129.0 x 79.5 mm, 235 parts (30 on the bottom side), 129 nets.

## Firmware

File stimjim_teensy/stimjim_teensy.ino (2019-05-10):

/* stimjim_teensy (c) Nathan Cermak 2019. */

#include <SPI.h>

#define MICROAMPS_PER_DAC 0.1017            // 20V * (1/(3000 V/A)) / 2^16 = 0.1uA / DAC unit
#define MICROAMPS_PER_ADC 0.85              //  (1/(100*(1+49.9k/1.8k) V/A)) * 20V / 2^13 = 0.85
#define MILLIVOLTS_PER_DAC 0.442            // 20V / 2^16 * gain of 1.45 ~= 0.44 mV / DAC unit
#define MILLIVOLTS_PER_ADC 2.44             // 20V / 2^13 = 2.44 mV / ADC unit

#define PT_ARRAY_LENGTH 10
#define MAX_NUM_STAGES 10

#define OE0_0 6
#define OE1_0 5
#define OE0_1 1
#define OE1_1 0
#define CS0_0 9
#define CS1_0 7
#define CS0_1 3
#define CS1_1 2
#define NLDAC_1 4
#define NLDAC_0 10
#define IN0 22
#define IN1 23
#define LED0 21
#define LED1 20
#define MISO_0 8
#define MISO_1 12

// ------------- SPI setup ------------------------------------- //
//AD5752 DAC runs at max 30MHz, SPI mode 1 or 2
SPISettings settingsDAC(10000000, MSBFIRST, SPI_MODE1); // Does not seem to work at 20MHz!
//AD7321 settings - clock starts high, data latch on falling edge
SPISettings settingsADC(5000000, MSBFIRST, SPI_MODE2);  // Can't run SPI clock faster than 1MHz without errors

// ------------- Serial setup ---------------------------------- //
char comBuf[1000];
int bytesRecvd;

// ------------- Compensation for various DC offsets ---------- //
int currentOffsets[2];
int voltageOffsets[2];

// --------- States of ADCs (set to read current or voltage?) ---//
volatile bool adcSelectedInput[2];

// ------------- PulseTrain parameter setup -------------------- //
struct PulseTrain {
  unsigned int mode[2];
  unsigned int period;                          // usec
  unsigned long duration;                       // usec

  int nStages;
  int amplitude[2][MAX_NUM_STAGES];             // mV or uA, depending on mode
  unsigned int stageDuration[MAX_NUM_STAGES];   // usec

  unsigned long trainStartTime;                 // usec
  int nPulses;
  int measuredAmplitude[4][MAX_NUM_STAGES];     // Ch0_V, Ch0_I, Ch1_V, Ch1_I
};
volatile PulseTrain PTs[PT_ARRAY_LENGTH];
volatile PulseTrain *activePT0, *activePT1;
IntervalTimer IT0, IT1;

// ------------ Globals for trigger status -------------------- //
int triggerTargetPTs[2];

// ------------ Function prototypes --------------------------- //
void setupADCs();
void setupDACs();
void setOutputMode(byte channel, byte mode);
void writeToDacs(int16_t amp0, int16_t amp1);
void writeToDac(byte channel, int16_t amp);
int readADC(byte channel, byte line);

void getCurrentOffsets();
void getVoltageOffsets();

int pulse (volatile PulseTrain* PT);
void printTrainResultSummary(volatile PulseTrain* PT);
void pulse0();
void pulse1();
void startIT0(int ptIndex);
void startIT0ViaInputTrigger();
void startIT1(int ptIndex);
void startIT1ViaInputTrigger();

void printPulseTrainParameters(int i);
volatile PulseTrain* clearPulseTrainHistory(volatile PulseTrain* PT);








void setOutputMode(byte channel, byte mode) {
  // mode 0-3 are: VOLTAGE, CURRENT, HIGH-Z, GROUND
  digitalWrite((channel) ? OE0_1 : OE0_0, (0b00000001 & mode) ? HIGH : LOW);
  digitalWrite((channel) ? OE1_1 : OE1_0, (0b00000010 & mode) ? HIGH : LOW);
}


void writeToDacs(int16_t amp0, int16_t amp1) {
  /* The input shift register is 24 bits wide, MSB first. The input register consists of 
   * a read/write bit, three register select bits, three DAC address bits, and 16 data bits.
   * Stimjim's AD5752 uses two's complement. */
  SPI.beginTransaction(settingsDAC);
  digitalWrite(CS0_0, LOW);
  SPI.transfer(0);
  SPI.transfer16(amp0);
  digitalWrite(CS0_0, HIGH);
  digitalWrite(CS0_1, LOW);
  SPI.transfer(0);
  SPI.transfer16(amp1);
  digitalWrite(CS0_1, HIGH);
  SPI.endTransaction();
  // latch data on both DACs
  digitalWrite(NLDAC_0, LOW);
  digitalWrite(NLDAC_1, LOW);
  digitalWrite(NLDAC_0, HIGH);
  digitalWrite(NLDAC_1, HIGH);
}


void writeToDac(byte channel, int16_t amp) {
  SPI.beginTransaction(settingsDAC);
  digitalWrite((channel) ? CS0_1 : CS0_0, LOW);
  SPI.transfer(0);     // write to AD5752 is 24-bit, first 8 low means output 0
  SPI.transfer16(amp);
  digitalWrite((channel) ? CS0_1 : CS0_0, HIGH);
  SPI.endTransaction();

  digitalWrite((channel) ? NLDAC_1 : NLDAC_0, LOW);
  digitalWrite((channel) ? NLDAC_1 : NLDAC_0, HIGH);
}


void setupADCs(float range) {
  SPI.beginTransaction(settingsADC);
  for (int i = 0; i < 2; i++) {
    int cs = (i == 0) ? CS1_0 : CS1_1; //CS1_x is ADC for channel x
    digitalWrite(cs, LOW); //[15] = write, [13] = range register
    if (range == 2.5){
      SPI.transfer16(0b1011000100000000); // write range register +-2.5V on both channels
    } else if (range == 5) {
      SPI.transfer16(0b1010100010000000);       // write range register +-5V on both channels)
    } else {
      SPI.transfer16(32768 + 8192);       // write range register, +-10V on both channels
    }
    digitalWrite(cs, HIGH);
    delayMicroseconds(1);
    digitalWrite(cs, LOW);
    SPI.transfer16(32768 + 16); // write control register, read channel 0 (voltage), use internal ref, 
    adcSelectedInput[i] = 0;
    digitalWrite(cs, HIGH);
  }
  SPI.endTransaction();
}

void setupDACs() {
  SPI.beginTransaction(settingsDAC);
  for (int i = 0; i < 2; i++) {
    int cs = (i == 0) ? CS0_0 : CS0_1; //CS0_x is DAC for channel x
    for (int j=0; j<2; j++){ // first write may be ignored due to undefined powerup state, so repeat 2x
      digitalWrite(cs, LOW); 
      SPI.transfer(8); // select "output range" register
      SPI.transfer16(4); // set mode as "+-10V mode (xxx...100)
      digitalWrite(cs, HIGH);
    }
    digitalWrite(cs, LOW);
    SPI.transfer(16); // select "power control" register
    SPI.transfer16(1); // set mode as dac_A powered up
    digitalWrite(cs, HIGH);
    delayMicroseconds(10);
  }
  SPI.endTransaction();
}



int readADC(byte channel, byte line) {
  
  int cs = (channel) ? CS1_1 : CS1_0;
  
  SPI.setMISO((channel)?MISO_1:MISO_0); // channels 0 & 1 use different MISO lines because isolators dont do tristate
  SPI.beginTransaction(settingsADC);
  digitalWrite(cs, LOW);
  if(adcSelectedInput[channel] != line){  // make sure we're reading the correct input (voltage or current)
    adcSelectedInput[channel] = line;
    SPI.transfer16(32768 + 16 + 1024*line);
    digitalWrite(cs, HIGH);
    digitalWrite(cs, LOW);
  }

  int data = SPI.transfer16(0) - (line ? 8192 : 0);
  digitalWrite(cs, HIGH);
  SPI.endTransaction();
  if (data > 4095)
    data -= 8192;
  return(data);
}


void getCurrentOffsets() {
  int adcReadSum[2];
  int bestDcVal[2] = {10000, 10000};

  setOutputMode(0, 3); // output grounded, Iout goes to ground via 1k on-board resistor
  setOutputMode(1, 3); // output grounded, Iout goes to ground via 1k on-board resistor
  setupADCs(2.5);
  for (int i = -100; i < 100; i++) {
    writeToDacs(i, i);
    delayMicroseconds(50);
    adcReadSum[0] = adcReadSum[1] = 0;
    for (int j = 0; j < 100; j++) {
      adcReadSum[0] += readADC(0, 1); // channel(0,1), line(V/I)
      adcReadSum[1] += readADC(1, 1);
    } 
    // Serial.print(i); Serial.print(","); 
    // Serial.print(adcReadSum[0]); Serial.print(","); Serial.println(adcReadSum[1]); 
    for (int channel = 0; channel < 2; channel++) {
      if (abs(adcReadSum[channel]) < bestDcVal[channel]) {
        currentOffsets[channel] = i;
        bestDcVal[channel] = abs(adcReadSum[channel]);
      }
    }
  }
  writeToDacs(currentOffsets[0], currentOffsets[1]);
  setupADCs(10);
  char str[40];
  sprintf(str, "Best current offsets: %d, %d\n", currentOffsets[0], currentOffsets[1]);
  Serial.print(str);
}


void getVoltageOffsets() {
  int adcReadSum[2];
  int bestDcVal[2] = {10000, 10000};

  setOutputMode(0, 0); // VOLTAGE OUTPUT - DANGEROUS
  setOutputMode(1, 0); // VOLTAGE OUTPUT - DANGEROUS
  setupADCs(2.5);
  for (int i = -100; i < 100; i++) {
    writeToDacs(i, i);
    delayMicroseconds(30);
    adcReadSum[0] = adcReadSum[1] = 0;
    for (int j = 0; j < 100; j++) {
      adcReadSum[0] += readADC(0, 0); // channel(0,1), line(V/I)
      adcReadSum[1] += readADC(1, 0);
    }
    // Serial.print(i); Serial.print(","); 
    // Serial.print(adcReadSum[0]); Serial.print(","); Serial.println(adcReadSum[1]); 
    for (int channel = 0; channel < 2; channel++) {
      if (abs(adcReadSum[channel]) < bestDcVal[channel]) {
        voltageOffsets[channel] = i;
        bestDcVal[channel] = abs(adcReadSum[channel]);
      }
    }
  }

  writeToDacs(voltageOffsets[0], voltageOffsets[1]);
  setOutputMode(0, 3); 
  setOutputMode(1, 3);
  setupADCs(10);
  char str[40];
  sprintf(str, "Best voltage offsets: %d, %d\n", voltageOffsets[0], voltageOffsets[1]);
  Serial.print(str);
}


int pulse (volatile PulseTrain* PT) {
  if (PT->nPulses == 0)
    PT->trainStartTime = micros();

  //check if the pulseTrain is finished; if so, exit
  if (micros() - PT->trainStartTime >= PT->duration)
    return 0;

  if (PT->mode[0] < 2)   setOutputMode(0, PT->mode[0]);
  if (PT->mode[1] < 2)   setOutputMode(1, PT->mode[1]);

  int dac0val, dac1val;
  for (int i = 0; i < PT->nStages; i++) {
    
    dac0val = PT->amplitude[0][i] / ((!PT->mode[0]) ? MILLIVOLTS_PER_DAC : MICROAMPS_PER_DAC) + ((PT->mode[0]) ? currentOffsets[0] : voltageOffsets[0]);
    dac1val = PT->amplitude[1][i] / ((!PT->mode[1]) ? MILLIVOLTS_PER_DAC : MICROAMPS_PER_DAC) + ((PT->mode[1]) ? currentOffsets[1] : voltageOffsets[1]);

    if (PT->mode[0] < 2 && PT->mode[1] < 2){
      writeToDacs(dac0val, dac1val);
    } else if (PT->mode[0] < 2){
      writeToDac(0, dac0val);
    } else if (PT->mode[1] < 2){
      writeToDac(1, dac1val);
    }
    
    long stageStartTime = micros();
    
    delayMicroseconds(30); // allow 30 us for output to settle

    // note: this limits bandwidth to do these reads (each requires 32 bytes at 5MHz SPI)
    if (PT->mode[0] < 2)
      PT->measuredAmplitude[0][i] += readADC(0, PT->mode[0] > 0) * ((PT->mode[0])?MICROAMPS_PER_ADC:MILLIVOLTS_PER_ADC); 
    if (PT->mode[1] < 2)
      PT->measuredAmplitude[1][i] += readADC(1, PT->mode[1] > 0) * ((PT->mode[1])?MICROAMPS_PER_ADC:MILLIVOLTS_PER_ADC); 
    
    //end this stage only once time since write reaches stage duration.
    while (micros() - stageStartTime < PT->stageDuration[i])
      continue;
  }
  // set DACs back to 0 voltage/current
  writeToDacs((PT->mode[0]) ? currentOffsets[0] : voltageOffsets[0],
              (PT->mode[1]) ? currentOffsets[1] : voltageOffsets[1]);
  
  // switch outputs to ground
  if (PT->mode[0] < 2)     setOutputMode(0, 3);
  if (PT->mode[1] < 2)     setOutputMode(1, 3);
  
  PT->nPulses++;
  return 1;
}


void printTrainResultSummary(volatile PulseTrain* PT) {
  Serial.print("Train complete. Delivered "); Serial.print(PT->nPulses);
  Serial.println(" pulses.\nCurrent/Voltage by stage: ");
  Serial.println("           Ch0                Ch1 ");
  char str[200];
  for (int i = 0; i < PT->nStages; i++) {
    Serial.print("Stage "); Serial.print(i);
    sprintf(str, "%6d%s,          ", PT->measuredAmplitude[0][i] / PT->nPulses, (PT->mode[0])?"uA":"mV");
    Serial.print(str);
    sprintf(str, "%6d%s,          ", PT->measuredAmplitude[1][i] / PT->nPulses, (PT->mode[1])?"uA":"mV");
    Serial.println(str);
  }
}

void pulse0() {
  if (!pulse(activePT0)) {
    IT0.end();
    printTrainResultSummary(activePT0);
    if(activePT0->mode[0] < 2)  digitalWrite(LED0, LOW);
    if(activePT0->mode[1] < 2)  digitalWrite(LED1, LOW);
  }
}

void pulse1() {
  if (!pulse(activePT1)) {
    IT1.end();
    printTrainResultSummary(activePT1);
    if(activePT1->mode[0] < 2)  digitalWrite(LED0, LOW);
    if(activePT1->mode[1] < 2)  digitalWrite(LED1, LOW);
  }
}

void startIT0ViaInputTrigger() {
  if (triggerTargetPTs[0] >= 0)
    startIT0(triggerTargetPTs[0]);
}
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

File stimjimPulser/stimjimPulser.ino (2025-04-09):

//    stimjimPulser (c) Nathan Cermak <cerman07 at protonmail.com>.
//
//    This file is part of stimjimPulser.
//
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

// Valid serial commands:
//    S - Set pulseTrain parameters. Example:
//        S0,0,1,1000,100000; 100,-100,100; -50,50,20;
//        1st argument (0) means set parameters for pulseTrain 0.
//        2nd argument (0) - mode 0 (voltage) on output channel 0 (see modes below under M)
//        3rd argument (1) - mode 1 (current) on output channel 1
//        4th argument (1000) - period of pulsetrain in microseconds. In example, run 1 pulse every ms.
//        5th argument (100000) - duration of pulsetrain in microseconds. In example, duration is 100 ms.
//        6th, 7th and 8th arguments - pulse stage 0 parameters
//            amplitudes for both channels (in uA and mV, depending on mode), and duration in usec.
//            In this case, sets amplitudes to 100uA, -100mV, for 100 microseconds
//        9th, 10th and 11th arguments - pulse stage 1 parameters
//            amplitudes for both channels (in uA and mV, depending on mode), and duration in usec.
//            In this case, sets amplitudes to 100uA, -100mV, for 100 microseconds
//        etc... for trios of arguments, up to 10 stages total.
//
//    T, U - T0 means start PulseTrain[0]. U0 also means start PulseTrain[0]. T and U can be
//           used to run two pulse train simultaneously.
//    B - measure ADC offset value (by grounding output and measuring ADC value on output).
//    C - measure current and voltage offsets by sweeping DAC values and reading output.
//    D - Print current values of all offsets (ADC, current, voltage)
//    R - R0,<n>,0 means that logic high on "input" 0 starts PulseTrain n.
//        R0,0,1 means that "input" 0 is reprogrammed as an output that marks stimulus start time of whatever pulsetrain is being delivered
//    M - M0,0 means set output mode for channel 0 to 0. output modes are as follows:
//        0 - voltage
//        1 - current
//        2 - disconnected (hi-z)
//        3 - grounded
//    A - A0,1000 means set amplitude on channel 0 to 1000 (dac units; -32,768 to +32,767)
//    V - V0,100 means set amplitude on channel 0 to 100mV
//    E - E0,1 means read channel zero, line 1. Line 0 is voltage out, line 1 is current sense.
//        Returns (prints over serial) value in raw adc units.
//    V - V0 means default serial reporting, V1 means verbose


#include <Stimjim.h>

#define PT_ARRAY_LENGTH 100
#define MAX_NUM_STAGES 10

// ------------- Serial setup ---------------------------------- //
char comBuf[1000];
int bytesRecvd;
bool verbose = false;

// ------------- PulseTrain parameter setup -------------------- //
struct PulseTrain {
    unsigned int mode[2];
    unsigned long period;                          // usec
    unsigned long duration;                       // usec

    int nStages;
    int amplitude[2][MAX_NUM_STAGES];             // mV or uA, depending on mode
    unsigned int stageDuration[MAX_NUM_STAGES];   // usec

    unsigned long trainStartTime;                 // usec
    int nPulses;
    int measuredAmplitude[4][MAX_NUM_STAGES];     // Ch0_V, Ch0_I, Ch1_V, Ch1_I
};


volatile PulseTrain PTs[PT_ARRAY_LENGTH];
volatile PulseTrain *activePT0, *activePT1;
IntervalTimer IT0, IT1;
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

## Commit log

2017-07-17 Initial commit
    - Includes ltspice simulations of basic circuit elements
    - Constant current source to 1.2 mA or so, +/-18V railes
    - Voltage compliance monitor
    - Charge offset regulation
    [microstim.sch]
2018-08-22 switched to kicad, new circuit design (mostly very similar to old).
    [BOM.ods, microstim.kicad_pcb]
2018-09-01 tons of updates - beginning of layout as well.
    [microstim.kicad_pcb, microstim.sch]
2018-09-02 first complete draft of microstim PCB. no errors in layout.
    [microstim.sch]
2018-09-02 Added bill of materials.
    [microstim_BOM.xlsx]
2018-09-02 added board name in silkscreen
    [microstim.kicad_pcb]
2018-09-02 added mounting holes
    [microstim.kicad_pcb]
2018-10-03 fixed some op-amps inserted backwards. also had to recommit everything due to OS upgrade and HD backup.
    [BOM.ods, microstim.kicad_pcb, microstim.sch, microstim_BOM.xlsx]
2018-10-13 redesign based on improved howland source at jon newmans suggestion
    [microstim.kicad_pcb, microstim.sch]
2018-10-14 lots of cleanup in file structure. nearly ready to order board v0.12. need to finish BOM and commit.
    [BOM.ods, microstim-B.Cu.gbl, microstim-B.Mask.gbs, microstim-B.SilkS.gbo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]
2018-10-14 added BOM, cleaned up junk files
    [microstim.kicad_pcb, microstim_BOM.xlsx]
2018-10-15 replaced LT1167 with INA826 instrument amp. hopefully this wasn't a terrible decision.
    [microstim-B.Cu.gbl, microstim-B.Mask.gbs, microstim-B.SilkS.gbo, microstim-Edge.Cuts.gm1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]
2018-10-15 forgot to add BOM
    [microstim_BOM.xlsx]
2018-10-16 possible an unsaved change to pcb?
    [microstim.kicad_pcb]
2018-10-20 updated BOM
    [microstim_BOM.xlsx]
2018-11-15 bunch of small fixes to board. havent yet regenerated gerbers. also added beginnings of teensy controller code.
    [microstim.kicad_pcb, microstim.sch, microstim_BOM.xlsx]
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2018-12-01 tons of changes - nearly done with pcb at 125x80mm (designed for slotted enclosure). now has 1) voltage output 2) voltage reading on ADC in both voltage output and current output modes. still need to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
    [microstim.kicad_pcb, microstim.sch]
2018-12-05 added datasheets for connector and enclosure. updated BOM. probably tons of updates to schematic/layout (cant remember when last commit was). layout/schematic complete - just need double-checking.
    [microstim.kicad_pcb, microstim.sch, microstim_BOM.xlsx]
2018-12-05 fixed logic bug and added explicit logic table to schematic
    [microstim.kicad_pcb, microstim.sch]
2018-12-10 major reorganization. also generated new gerbers for main board, panel, and combined pcb (board+panels).
    [CombinedPCB-B.Mask.gbs, CombinedPCB-B.Paste.gbp, CombinedPCB-B.SilkS.gbo, CombinedPCB-Bottom.gbl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]
2019-01-23 BOM had 0402 resistors, which should have been 0603. now fixed.
    [microstim_BOM.xlsx]
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2019-01-24 updated readme, fixed BOM cost column for boards
    [microstim_BOM.xlsx]
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2019-02-07 almost done with revision 3. 12v regs removed, GPIO breakout and indicator LEDs added, layout cleaned up
    [microstim.kicad_pcb, microstim.sch]
2019-02-08 major updates to isolate each output channel.
    [microstim.kicad_pcb, microstim.sch]
2019-02-09 making progress on layout... slowly
    [microstim.kicad_pcb, microstim.sch]
2019-02-09 getting darn close to done with layout.
    [microstim.kicad_pcb, microstim.sch]
2019-02-10 finished layout, schematic+pcb pdfs, BOM. need to do panels.
    [microstim.kicad_pcb, microstim.sch, microstim_BOM.xlsx]
2019-02-11 merged in benchmarking into v3b. changed 3.3v power pin so that design is compatible with teensy 3.1/2 and 3.5/6.
    [microstim.kicad_pcb, microstim.sch]
2019-02-11 a few unsaved changes in pcb?
    [microstim.kicad_pcb]
2019-02-12 updates to benchmarking parameter sets and analysis code
    [paramMat.csv]
2019-02-16 increased board size to 129x79.5 from 124.5x79.5, changed enclosure to something on digikey rather than newark. also added trigger capability to teensy code
    [microstim.kicad_pcb, microstim_BOM.xlsx]
2019-02-25 boatload of updates via jons suggestions. de-isolated grounds via large resistors+capacitors (to prevent static buildup on animal or issues with large discharges). increased resistor values in voltag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
    [microstim.kicad_pcb, microstim.sch, microstim_BOM.xlsx, panels.kicad_pcb]
2019-02-25 changed name to stimjim. added logo-ish thing to board silkscreen. changed ground coupling caps/resistors slightly. renamed a bunch of stuff and replaced most instances of word microstim with stimjim
    [microstim.kicad_pcb, microstim.sch, microstim_BOM.xlsx]
2019-02-25 renamed stuff and forgot to readd it git proj. now added
    [stimjim.kicad_pcb, stimjim.sch, stimjim_BOM.xlsx]
2019-02-25 BOM finally up to date!
    [stimjim_BOM.xlsx]
2019-02-25 made combined pcb layout (panel+mainpcb), added fab files
    [CombinedPCB-B.Cu.gbl, CombinedPCB-B.Mask.gbs, CombinedPCB-B.Paste.gbp, CombinedPCB-B.SilkS.gbo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]
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2019-03-21 replaced terrible 24-pin female header (too tight) with a better 24-pin female header in BOM
    [stimjim_BOM.xlsx]
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2019-06-05 missed renaming isolated MOSI nets on last try. fixed now.
    [stimjim.kicad_pcb, stimjim.sch]
2019-07-02 cleaned up layout, added tons of vias for proes, finished four layers. also fixed ch0/ch1 being backwards (fixed in master a while back)
    [stimjim.kicad_pcb, stimjim.sch]
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2019-08-06 (1) reverted paramMat and paramStringFile to previous grid (smallest pulse 200mV/20uA). (2) changed ISO7341->ISO7741, AD8276->AMP03, C10,36 680nF->1uF, requiring changes in BOM, schematic, schematic.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
    [paramMat.csv, stimjim.kicad_pcb, stimjim.sch, stimjim_BOM.xlsx]
2019-08-31 replaced 0.5% resistors in voltage output with 0.1% (updated BOM), changed gain in lib file, added more documentation to stimjimPulser, added manual voltage control mode.
    [stimjim_BOM.xlsx]
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2019-10-24 removed old datasheet files. fixed figure 1 schematic (misplaced resistor in improved howland pump diagram).
    [stimjim.kicad_pcb]
2019-11-01 push-terminal connectors J6 and J8 somehow missing from BOM - fixed!
    [stimjim_BOM.xlsx]
2019-11-01 fixed missing pin indicator on U22 in kicad-pcb file, regenerated fabrication (gerber) files. updated README to clarify separate ordering of main-board PCB and panel PCB.
    [stimjim.kicad_pcb]
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2020-06-14 updated 78L05 regulator to replace obsolete part
    [stimjim_BOM.xlsx]
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2020-10-18 updated kicad design to meet seeedstudio DFM requirements: (1) fixed DC/DC converter footprint and hole size (2) fixed through-hole size of GPIO 2x8 pin header footprint
    [stimjim.kicad_pcb, stimjim.sch]
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2023-11-17 Merged in nc-update-to-kicad7 (pull request #3)
    Update PCB design to kicad 7
    * migrate to kicad7
    * remove empty.kicad_wks; fix sheet size and add authors and version to page
    * migrate libraries to new format; fix incorrectly rescued symbols (+3.3V power flag and L78L05-SO8 regulator)
    * slowly fixing all ERC errors; down to 3
    * fix ina826 symbol (again). down to 0 ERC errors; 56 warnings
    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
    [panels.kicad_pcb, stimjim.kicad_pcb, stimjim.kicad_sch, stimjim.sch]
2023-11-17 Merged in nc-move-channels-to-subsheet (pull request #4)
    Move channel schematic to subsheet, make two instances of it. Fix the ERC and DRC errors I made.
    [channel.kicad_sch, panels.kicad_pcb, stimjim.kicad_pcb, stimjim.kicad_sch]
2024-05-31 Minor edits to PCB
    - Expose access to program button at test point that can be soldered to
    pin 28 using a wire
    - Increase tolerance on tight digital trace routing
    - Add keepout area to top copper at the point where the shield on the
    isolated DC power supply comes in close proximity to isolated ground.
    [channel.kicad_sch, stimjim.kicad_pcb, stimjim.kicad_sch]
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2025-12-06 Replace teensy with RP235xB
    [channel.kicad_sch, mcu.kicad_sch, stimjim-CuBottom.gbr, stimjim-CuIn1.gbr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]
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2026-01-17 fix curve in silkscreen
    [panels.kicad_pcb]
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2026-04-10 Rev C First Draft
    - Fix and move LED footprints
    - Move bar code sticker
    - Add op-amp unity voltage follower to ADC input
    - Remove screw terminals
    - Made panel screw holes bigger both panels (3.2mm -> 3.7mm) for 3.4mm
    screws
    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
    [EXN-23359.DXF, channel.kicad_sch, mcu.kicad_sch, panel-back.kicad_pcb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]
2026-05-27 Replace amplifiers
    - INA826 -> AD8421
    - AMP03 -> LT1995 w/ op-amp in feedback circuit
    - Also:
    - update to kicad v10
    - utilize multi-channel layout feature
    - update calculations on schematic
    [channel.kicad_sch, mcu.kicad_sch, stimjim.kicad_pcb, stimjim.kicad_sch]
2026-05-28 fix panel outline
    Remove the finer features that might not
    adhere to best practices for PCB DFM
    [EXN-23359.DXF, panel-back-B_Cu.gbr, panel-back-B_Mask.gbr, panel-back-Edge_Cuts.gbr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]
2026-06-08 tolerance resistors
    [channel.kicad_sch, stimjim.kicad_pcb]

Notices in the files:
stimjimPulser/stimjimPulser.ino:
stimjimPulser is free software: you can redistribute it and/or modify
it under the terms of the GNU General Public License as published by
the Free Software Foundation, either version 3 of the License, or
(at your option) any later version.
